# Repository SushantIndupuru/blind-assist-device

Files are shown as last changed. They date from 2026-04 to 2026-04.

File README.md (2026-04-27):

Ultrasonic Obstacle Detection Device

A low-cost wearable that helps visually impaired individuals detect nearby obstacles through haptic feedback. Two ultrasonic sensors drive left/right vibration feedback independently so users can tell which side a hazard is on.

Built and tested at the Calcutta Blind School. Full details in our paper (see below).

---

Hardware

| Component | Qty |
|---|---|
| Arduino Nano | 1 |
| HC-SR04 Ultrasonic Sensor | 2 |
| Coin Vibration Motor | 2 |
| Custom PCB | 1 |
| Li-Po Battery 3.7V 1000mAh | 1 |
| Buck-Boost Converter | 1 |
| 3D-Printed Case (`hardware/cad/blindsonnarcase.step`) | 1 |
| Wrist strap | 1 |

[Full Bill of Materials](hardware/BOM.xlsx) - ~$18.70 per unit total.

---

Wiring

Pin mapping is defined in `src/config.h`:

| Arduino Pin | Component |
|---|---|
| D8 | Left HC-SR04 TRIG |
| D9 | Left HC-SR04 ECHO |
| D6 | Right HC-SR04 TRIG |
| D7 | Right HC-SR04 ECHO |
| D3 (PWM) | Left motor channel 1 |
| D2 (PWM) | Left motor channel 2 |
| D5 (PWM) | Right motor channel 1 |
| D4 (PWM) | Right motor channel 2 |
| D13 | Status LED |
| VIN | Buck-boost output |
| GND | Common ground |

---

Firmware Build and Upload (PlatformIO)

This repository uses PlatformIO (not an Arduino `.ino` sketch).

1. Build (release): `pio run -e release`
2. Upload (release): `pio run -e release -t upload`
3. Serial monitor (9600 baud): `pio device monitor -b 9600`

Available environments in `platformio.ini`:

- `debug` (`-Og -g2 -DDEBUG`)
- `release` (`-Os -DNDEBUG`)

Board/framework defaults:

- Board: `nanoatmega328new`
- Framework: `arduino`
- Upload speed: `115200`

No external libraries are required.

---

Repo Structure

```
blind-assist-device/
├── hardware/
│   ├── BOM.xlsx
│   ├── stl/                        # 3D-printable case
│   └── pcb/                        # Gerber and drill/manufacturing outputs
├── src/                            # Firmware source files
```

---

Paper

For full system design, experimental results, and discussion:

> Ray, R. & Indupuru, S. (2025). *Ultrasonic Obstacle Detection Device.* [link]

---

Acknowledgments

Thank you to the participants at the Calcutta Blind School who volunteered to test this prototype.

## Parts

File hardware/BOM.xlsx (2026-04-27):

 | Ultrasonic Obstacle Detection Device — Bill of Materials
 | Calcutta Blind School Prototype • Rishab Ray & Sushant Indupuru
# | Component | Supplier / Part | Qty | Unit Cost ($) | Line Total ($) | Notes
 | Microcontroller & PCB
1 | Arduino Nano | Arduino / generic clone | 1 | $2.50 | $2.50 | ATmega328P; controls sensors & motors
2 | Custom PCB | Local fabrication (India) | 1 | $5.00 | $5.00 | User-supplied estimate; bulk lowers cost
 | Sensing
3 | HC-SR04 Ultrasonic Sensor | SparkFun / generic | 2 | $1.20 | $2.40 | 15° FOV; 5 cm – 3.35 m range; 40 kHz
 | Power
4 | Li-Po Battery 3.7 V 1000 mAh | Generic | 1 | $3.50 | $3.50 | ~25 min runtime; JST connector
5 | Buck-Boost Converter | Generic module | 1 | $1.20 | $1.20 | Stable voltage for MCU & motors
6 | Battery Charger (one-time) | Generic TP4056 | 1 | $3.48 | $3.48 | One-time cost; not in per-unit total
 | Actuation
7 | Vibration Motor (coin type) | Generic | 2 | $0.80 | $1.60 | One per sensor; independent PWM control
 | Passives & Connectors
8 | Resistors (assorted) | Generic pack | 1 | $0.30 | $0.30 | Current limiting for motors/LEDs
9 | Diodes | 1N4148 or similar | 2 | $0.10 | $0.20 | Flyback protection for motors
10 | Transistors (NPN) | 2N2222 or similar | 2 | $0.15 | $0.30 | Motor drive switching
11 | Pin headers / connectors | Generic | 1 | $0.40 | $0.40 | Sensor & motor interface
 | Enclosure & Wearable
12 | 3D-printed case | PLA filament | 1 | $0.80 | $0.80 | STL files in repo /hardware/stl/
13 | Wrist strap + hardware | Generic | 1 | $0.50 | $0.50 | Velcro or nylon; harness for wrist mount
 | TOTAL (incl. charger) |  |  |  | $22.18 | All components
 | PER-UNIT (excl. charger) |  |  |  | $18.70 | Charger is one-time purchase

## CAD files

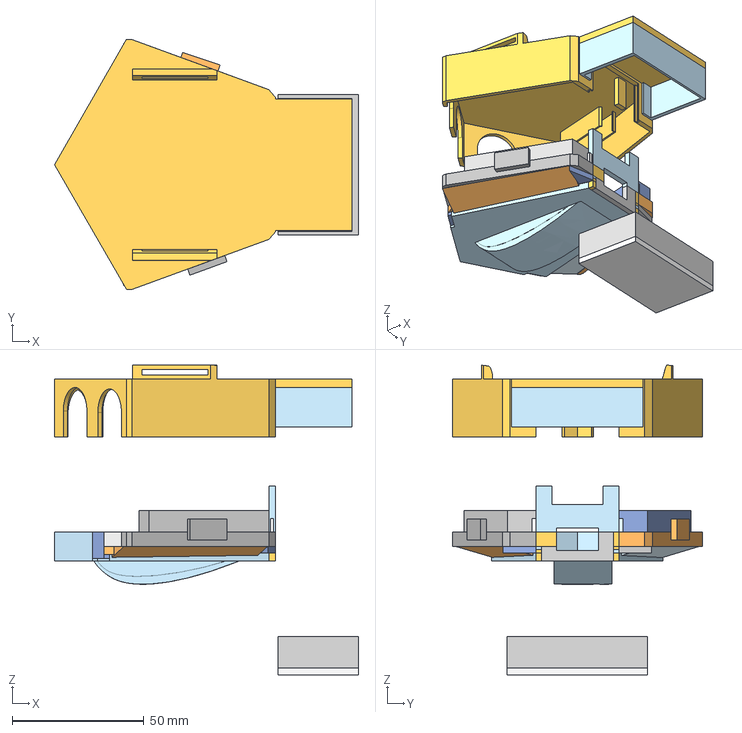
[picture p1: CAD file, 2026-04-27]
hardware/cad/blindsonnarcase.step
115.4 x 94.8 x 117.5 mm

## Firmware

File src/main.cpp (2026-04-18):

#include <Arduino.h>
#include "config.h"
#include "UltrasonicSensor.h"
#include "HapticMotor.h"

// ── Objects ───────────────────────────────────────────────────────────────────

UltrasonicSensor leftSensor(LEFT_TRIG_PIN, LEFT_ECHO_PIN, "LEFT", SMOOTHING_SAMPLES);
UltrasonicSensor rightSensor(RIGHT_TRIG_PIN, RIGHT_ECHO_PIN, "RIGHT", SMOOTHING_SAMPLES);

HapticMotor leftMotor(LEFT_MOTOR_PIN_1, LEFT_MOTOR_PIN_2);
HapticMotor rightMotor(RIGHT_MOTOR_PIN_1, RIGHT_MOTOR_PIN_2);

// ── Helpers ───────────────────────────────────────────────────────────────────

// Map a smoothed distance (cm) to a PWM vibration level.
uint8_t distanceToVibration(float distanceCm) {
  if (distanceCm < 0) return MIN_VIBRATION;
  if (distanceCm <= MIN_DISTANCE_CM) return MAX_VIBRATION;
  if (distanceCm >= MAX_DISTANCE_CM) return MIN_VIBRATION;
  return map(distanceCm, MIN_DISTANCE_CM, MAX_DISTANCE_CM, MAX_VIBRATION, MIN_VIBRATION);
}

void updateStatusLed() {
  bool leftClose = leftMotor.getLevel() > CLOSE_THRESHOLD;
  bool rightClose = rightMotor.getLevel() > CLOSE_THRESHOLD;
  digitalWrite(STATUS_LED_PIN, (leftClose || rightClose) ? HIGH : LOW);
}

void printStatus() {
  bool leftClose = leftMotor.getLevel() > CLOSE_THRESHOLD;
  bool rightClose = rightMotor.getLevel() > CLOSE_THRESHOLD;

  Serial.print(" | L=");
  Serial.print(leftMotor.getLevel());
  Serial.print(" R=");
  Serial.print(rightMotor.getLevel());

  if (leftClose && rightClose) Serial.println(" | BOTH SIDES CLOSE");
  else if (leftClose) Serial.println(" | LEFT CLOSE");
  else if (rightClose) Serial.println(" | RIGHT CLOSE");
  else Serial.println(" | CLEAR");
}

void testMotors() {
  Serial.println("Testing motors...");
  leftMotor.setLevel(100);
  rightMotor.setLevel(100);
  delay(300);
  leftMotor.setLevel(0);
  rightMotor.setLevel(0);
  Serial.println("Motor test done.");
}

// ── Setup ─────────────────────────────────────────────────────────────────────

void setup() {
  Serial.begin(9600);
  Serial.println("=== Sonar Haptic Device ===");

  leftSensor.begin();
  rightSensor.begin();
  leftMotor.begin();
  rightMotor.begin();

  pinMode(STATUS_LED_PIN, OUTPUT);

  // Startup blink
  for (int i = 0; i < 3; i++) {
    digitalWrite(STATUS_LED_PIN, HIGH);
    delay(100);
    digitalWrite(STATUS_LED_PIN, LOW);
    delay(100);
  }

  testMotors();

  Serial.println("Running. Each sensor alternates every " + String(SENSOR_POLL_INTERVAL_MS) + "ms.");
  Serial.println("----------------------------");
}

// ── Loop ──────────────────────────────────────────────────────────────────────

void loop() {
  static unsigned long lastPollTime = 0;
  static bool readLeftNext = true;

  unsigned long now = millis();
  if (now - lastPollTime < SENSOR_POLL_INTERVAL_MS) return;
  lastPollTime = now;

  if (readLeftNext) {
    leftSensor.read();
    float dist = leftSensor.getSmoothedDistance();
    leftMotor.setLevel(distanceToVibration(dist));

    Serial.print("LEFT: ");
    if (dist < 0) Serial.print("TIMEOUT");
    else {
      Serial.print(dist, 1);
      Serial.print("cm");
    }
    Serial.print(" -> vib=");
    Serial.print(leftMotor.getLevel());
  } else {
    rightSensor.read();
    float dist = rightSensor.getSmoothedDistance();
    rightMotor.setLevel(distanceToVibration(dist));

    Serial.print("RIGHT: ");
    if (dist < 0) Serial.print("TIMEOUT");
    else {
      Serial.print(dist, 1);
      Serial.print("cm");
    }
    Serial.print(" -> vib=");
    Serial.print(rightMotor.getLevel());
  }

  printStatus();
  updateStatusLed();

  readLeftNext = !readLeftNext;
}

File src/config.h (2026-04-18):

#pragma once

// ── Sensor pins ──────────────────────────────────────────────────────────────
#define LEFT_TRIG_PIN   8
#define LEFT_ECHO_PIN   9
#define RIGHT_TRIG_PIN  6
#define RIGHT_ECHO_PIN  7

// ── Motor pins ────────────────────────────────────────────────────────────────
#define LEFT_MOTOR_PIN_1  3
#define LEFT_MOTOR_PIN_2  2
#define RIGHT_MOTOR_PIN_1 5
#define RIGHT_MOTOR_PIN_2 4

// ── Status LED ────────────────────────────────────────────────────────────────
#define STATUS_LED_PIN 13

// ── Distance thresholds (cm) ──────────────────────────────────────────────────
#define MIN_DISTANCE_CM  5
#define MAX_DISTANCE_CM  250

// ── Vibration range (PWM 0–255) ───────────────────────────────────────────────
#define MIN_VIBRATION 0
#define MAX_VIBRATION 50

// ── Timing ────────────────────────────────────────────────────────────────────
// How often to poll one sensor (ms). Both sides are read in alternating cycles,
// so each side updates at 2× this interval.
#define SENSOR_POLL_INTERVAL_MS 100

// ── Smoothing ─────────────────────────────────────────────────────────────────
#define SMOOTHING_SAMPLES 3

// ── Alert threshold ───────────────────────────────────────────────────────────
// Vibration level above which we consider an object "close" for LED/Serial warnings.
#define CLOSE_THRESHOLD 100

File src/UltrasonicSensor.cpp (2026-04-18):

#include "UltrasonicSensor.h"

UltrasonicSensor::UltrasonicSensor(uint8_t trigPin, uint8_t echoPin, const char *name,
                                   uint8_t smoothingSamples, unsigned long timeoutUs)
    : _trigPin(trigPin), _echoPin(echoPin), _name(name),
      _timeoutUs(timeoutUs), _smoothingSamples(smoothingSamples), _historyIndex(0) {
    _history = new float[_smoothingSamples];
    for (uint8_t i = 0; i < _smoothingSamples; i++) {
        _history[i] = -1;
    }
}

void UltrasonicSensor::begin() {
    pinMode(_trigPin, OUTPUT);
    pinMode(_echoPin, INPUT);
}

float UltrasonicSensor::read() {
    float distance = _readRaw();
    _history[_historyIndex] = distance;
    _historyIndex = (_historyIndex + 1) % _smoothingSamples;
    return distance;
}

float UltrasonicSensor::getSmoothedDistance() const {
    return _computeSmoothed();
}

float UltrasonicSensor::_readRaw() {
    digitalWrite(_trigPin, LOW);
    delayMicroseconds(2);
    digitalWrite(_trigPin, HIGH);
    delayMicroseconds(10);
    digitalWrite(_trigPin, LOW);

    long duration = pulseIn(_echoPin, HIGH, _timeoutUs);
    if (duration == 0) return -1;

    return (duration * 0.0343f) / 2.0f;
}

float UltrasonicSensor::_computeSmoothed() const {
    float sum = 0;
    uint8_t count = 0;
    for (uint8_t i = 0; i < _smoothingSamples; i++) {
        if (_history[i] >= 0) {
            sum += _history[i];
            count++;
        }
    }
    return (count > 0) ? sum / count : -1;
}
